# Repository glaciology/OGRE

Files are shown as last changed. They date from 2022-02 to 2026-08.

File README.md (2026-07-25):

<p align="center">

 
 </p>

# Open GNSS Research Equipment :: A low-power, low-cost GNSS data logger for monitoring the cryosphere.
<p align="center">

</p>

## Overview
Originally designed for easily logging multi-GNSS data in remote regions of the Arctic, this instruments incorporates low-power, low-cost components onto a single circuit board and features a Ublox ZED-F9P/X20P GNSS module and Ambiq Apollo3 MCU. By stripping away many of the features of commercial options, we streamline this instrument specifically for "set it and forget it" rapid deployments, acquiring high quality GNSS data.
- Logs GPS, GLONASS, BEIDOU, GALILEO & Satellite Nav Messages to a microSD, which can be easily converted to standard RINEX format (from .ubx) for positioning with PPK or PPP (RTK is possible but DIY). F9P variants (hardware v1.0) log L1/L2, X20P variant logs L1/L2/L5 (hardware v2.0). 
- Easily configurable via microSD card. Many configuration options to optimize data and battery needs, such as a polar-specific mode of daily logging during summertime and weekly logging during the winter, or a sunrise/sunset mode for logging data for 3 hours, twice daily to capture diurnal glacial signals. 
- Low cost, totaling ~$175, not including external components. PCB inside enclosure measures 7x6.5x2.5cm. 
- Current consumption with a 12V supply is 45-65mA (.5-.8W) awake, and 0.07mA (.8mW) asleep. We have used a single 12V 40Amp hr battery with a 10W solar panel to log continuously for 3 hours a day every day, including throughout the long polar night in Greenland.
- Programmed in Arduino environment, for easy customization.

A detailed guide is maintained [here](https://docs.google.com/document/d/1q8-jAFY2cO8MIOHwoCQhJwPjmURbkkGEsrDBrOs5gMM/edit?usp=sharing). 

<p align="center">

</p>

## Project Organization 
[Software: Contains Arduino Code and Test Scripts](Software/)
- [OGRE: Software and software config files for upload to OGRE instrument](Software/OGRE) <br>
[Hardware: Hardware & Manufacturing Files](Hardware/)
- Here you will find the component lists for OGREv1 and OGREv2. We recommend all future acquisitions use OGREv2, which is optimized for the X20P reciever. However, use v1 if you or your manufacturer cannot flash the device using a SWD/JTAG interface. See the firmware section for details on flashing the correct firmware onto your v1 or v2 device.  

Again, a detailed, up-to-date guide can found [here](https://docs.google.com/document/d/1q8-jAFY2cO8MIOHwoCQhJwPjmURbkkGEsrDBrOs5gMM/edit?usp=sharing)!

## Getting Started 

The OGRE has the following modes of operation (note, not all modes are available on old versions of the firmware, upgrade may be necessary): 
  - (1) Daily Fixed Mode: Log GNSS data same time every day, starting & ending during USER-defined start/stop hours, OR
  - (2) Continous Mode: Log GNSS data continously (new file generated at each midnight UTC), OR
  - (3) Monthly Mode: Log GNSS data for 24 hours on a USER-specified day (1-28) each month, OR
  - (4) Interval Mode: Each 24-hour log session is spaced by a USER-defined interval (e.g., log every 3 days for 24 hours), OR
  - (5) Log GNSS data for 24 hours on USER specified dates/times read from a .txt file. Defaults to mode 4 after last user-provided date.
  - (6) Log GNSS data for 24 hours; During winter once on every Nth day (or USER-defined interval, in # of days); During summer daily. "Summer" is May-August (or USER-defined months).
  - (7) Reserved.
  - (8) Log GNSS data twice daily for USER specified duration, during-USER defined morning period and USER-defined evening. 
  - (99) Test Mode: Used for development. Log GNSS data for 50 second interval, sleep for 50 second and repeat.
  
OUTPUTs: With all modes, GNSS data (phase, doppler, SNR, nav message etc.) are logged to a uSD card in .ubx (UBLOX) proprietary format. Under open sky conditions, we found that an epoch of data (1s) is ~2000-3000 bytes. If logging at 15 seconds for a year, this equates to 6GB of data. A debug file is also generated after each log session is closed, reporting the health of the system (temperature, battery voltage, logging errors, etc.). 
  
INPUTs: USERS specify settings in the CONFIG.txt file, which, if uploaded to the SD card, will be read into the software. If no CONFIG.txt exists on the attached SD card, it will automatically be added to the SD card with the default settings upon initial power-on.
Otherwise, software will default to hardcoded configuration. USER may also upload a EPOCH.txt file, which allows the user to specify up to 20 log dates (unix epoch format) for logging in Mode 5. The CONFIG.txt and EPOCH.txt files are Windows and Mac (e.g., Notepad or Textedit) compatable (previously, carriage return characters \n caused issues for Windows-generated files). Using an older CONFIG.txt version will not crash the OGRE, but will cause the OGRE to use the default settings instead. 

The CONFIG.TXT file is formatted as follows (make sure to use the right version, or let the device auto-populate the template onto your SD card): 

```
LOG_MODE(1: daily hr, 2: cont, 3: mon, 4: 24 roll, 5: date, 6: season, 99: test)=2
LOG_START_HOUR_UTC(mode 1 only)=17
LOG_END_HOUR_UTC(mode 1 only)=23
LOG_START_DAY(mode 3 only, 0-28)=25
LOG_EPOCH_SLEEP(modes 4/5 only, seconds)=3600
LED_INDICATORS(0-false, 1-true)=1
MEASURE_BATTERY(0-false, 1-true)=0
ENABLE_GPS(0-false, 1-true)=1
ENABLE_GLO(0-false, 1-true)=1
ENABLE_GAL(0-false, 1-true)=1
...
...
...
...
```

- If the USER selects LOG_MODE=1, then LOG_START_HOUR_UTC and LOG_END_HOUR_UTC must be specified. 
- If the USER selects LOG_MODE=3, then LOG_START_DAY must also be specified (day of each month GNSS data is logged). 
- If the USER selects LOG_MODE=5, then unix epoch dates for logging are specified in EPOCH.txt. If no dates are specified or if all dates have elapsed, then log interval defaults to LOG_MODE 4, where LOG_EPOCH_SLEEP must be defined.
- If the USER selects LOG_MODE=6, the instrument logs continuously during SUMMER_START_MONTH + SUMMER_START_DAY through SUMMER_END_MONTH + SUMMER_END_DAY (inclusive). Furthermore, the duration between logging during winter is set by WINTER_INTERVAL. Note: log sessions are 24 hours.
- If the USER selects LOG_MODE=8, then LOG_START_HOUR_UTC and LOG_END_HOUR_UTC must be specified, along with LOG_START_HR_TWO and LOG_END_HR_TWO. 
- LED_INDICATORS, if false, will disable all LEDs, excluding those present during initialization. 
- MEASURE_BATTERY, if true, battery voltage is measured/monitored, and the instrument will be put to sleep when voltage dips below 10.9V (OR as defined by user in BAT_SHUTDOWN_V). System will restart when voltage measured above ~11.2V (or 0.5V above BAT_SHUTDOWN_V). 
- STATION_NAME is a number between 0000 and zzzz (no special characters, please!), and will be appended to the timestamped file names for each GNSS file.
- MEASURE_RATE is frequency of epoch solutions logged to SD card: 1 = 1 solution per second, 15 = 1 solution per 15 seconds. Range is .5 to 60 (seconds). 

BASIC OPERATION:  
Insert the uSD card (with or without CONFIG & EPOCH files), then connect battery to +/- sides of the screw terminal. The system will attempt to initialize and following LED indicators will flash: 
  - 1 Hz Blinks: System acquiring GPS time and attempting to sync real time clock (RTC).
  - 10 rapid Blinks: System Configuration Complete!
  
 The following LED patterns indicate success or failure for OGREv2. For OGREv1, there is only 1 led. 
| Pattern | Meaning | Color (v2) | Triggered From |
|---|---|---|---|
| 2 blink pattern, then waits for reset | microSD card failed to initialize (twice) | 🔴 Red (`LED`) | `configureSD()` |
| 3 blink pattern, then waits for reset | u-blox I2C not detected, or GNSS constellation config failed | 🔴 Red (`LED`) | `configureGNSS()` |
| 5 blink pattern, then waits for reset | RTC failed to sync with GNSS within 3-minute window | 🔴 Red (`LED`) | `syncRtc()` |
| 6 rapid blinks | `CONFIG.TXT` missing/unreadable — using hard-coded defaults | 🔴 Red (`LED`) | `getConfig()` |
| 10 blinks | RTC synced + system configuration complete (boot only) | 🟡 Yellow (`LED2`) | `setup()` |
| 1 blink, roughly every 12 seconds | Device sleeping between sessions | 🔴 Red (`LED`) | `loop()` |
| 1 Hz blink | Acquiring GNSS fix during RTC sync | 🟡 Yellow (`LED2`) | `syncRtc()` |
| Rapid, irregular blinks while active, approx. corresponding to logging rate | Actively logging GNSS data to SD | 🔴 Red (`LED`) | `logGNSS()` |
| No blinks at all | Deep sleep — battery below shutdown threshold | *(none — both LEDs off)* | `checkBattery()` / `goToSleep()` |

## Software Upload
For OGREv1, software is uploaded using a USB-to-Serial converter. 
For OGREv2, software is uploaded using JTAG/SWD, or, if the proper bootloader is installed on the MCU, can be done over USB-to-Serial.

Only do this if you want to update the firmware on the OGRE, or if the OGRE has not yet had the firmware installed. A pre-compiled binary file is available with each release (see [releases](https://github.com/glaciology/OGRE/releases/)). Note: there are separate binaries for v1 and v2 OGREs. This binary file included in the release can be uploaded to the Apollo MCU (OGREv1) with a usb-to-serial cable connected to the PCB header pins using the Sparkfun Apollo3 Uploader [here](https://github.com/sparkfun/Apollo3_Uploader_SVL). 

For v2 OGREs, please reach out to me if you have questions that come up. The HARDWARE_VERSION macro must be set properly when manually compiling the code.

### OGRE V1
The USB to Serial converter is attached to the OGRE via the 5 through-hole pins on the PCB: attach Ground to GND, RX -> TX, TX->RX, etc. NOTE: the serial converter must be 3.3V. DO NOT EXPOSE pins to 5V. 

Example command line prompt using the svl.py script: [use baud -b 115200; provide path to binary file OGRE.ino.bin; find path of usb serial converter port by typing ls /dev/tty.* on Linux and selecting the proper usb port.] 
```
python3 svl.py -b 115200 -f /PATH/TO/BINARY/FILE/OGRE.ino.bin /dev/tty.usbserial-####
```

You can also compile the source code with the Arduino IDE, ensuring that the code and board libraries match the proper versions defined in the header of OGRE.ino [Sparkfun Artemis Module v1.2.3, SDFat library v2.1.0, Sparkfun ublox GNSS library v2.2.8]. 

### OGRE V2
If the bootloader is installed on OGRE v2, you can follow the above steps (same as OGRE v1). Otherwise, or if you don't know what I mean by this, you'll have to use JTAG/SWD. More details to come...

## Hardware Notes
<p align="center">

</p>

MATERIALS
Cost of PCB and all components totals ~$175. Detailed list of components found in the Hardware folder. <br>

ASSEMBLY
Assembly services are available through PCBWay, and the OGRE can be ordered directly from [here](https://www.pcbway.com/project/shareproject/OGRE_Open_GNSS_Research_Equipment_Receiver_33a809f3.html) for V1 or from [here](https://www.pcbway.com/project/shareproject/OGRE_Open_GNSS_Research_Equipment_v2_0_82247d12.html) for V2. Note that this assembly service often does not include the [Pololu](https://www.pololu.com/product/3792) component, which must be soldered (4 through-hole) by the user (requests may be made to PCBWay to see if they can source this component, or the user can ship to PCBWay). The user must also program the device following the instructions from the Software Upload section. OGRE2.0 (with ublox X20P) can similarly be ordered from [here](https://www.pcbway.com/project/shareproject/OGRE_Open_GNSS_Research_Equipment_v2_0_82247d12.html), and we highly recommend the customer asks PCBWay to upload the .bin firmware to the board using their JTAG/SWD interface. Instructions for PCBWay upload can be found [in Upload_Instructions](/Hardware/OGRE_v2.0/). 

If you choose to use a u-blox antenna, you will need a ground plane, which you can make out of any metal disc, or you can order pre-drilled discs from PCBWay too, [here](https://www.pcbway.com/project/shareproject/Ground_Plane_for_ublox_L1_L2_L5_GNSS_antenna_c3519487.html), compatitble for both L1/L2 and L1/L2/L5 versions of their antennas.

POWER REQUIREMENTS: 
In standard configuration, this system is powered by a 12V lead-acid battery. 
  
While this system is optimized for 12V batteries, input voltage can range from 5.2V to 20V with the following considerations/customizations:  
  - The DC-DC converter minimum input is 5.2V and maximum input is 50V, although additional power filtering at high voltages is required. 
  - The Battery Measurement circuit features a voltage divider circuit that must scale max voltage to 3.3V for the ADC pin. Standard dividers for a 12V battery use 68kOhm and 10kOhm resistors. USER may wish to adjust gain/offset of ADC battery measurement conversion in software if using non-standard (5.2-20V) power configuration. 
  - The reverse polarity protection MOSFET has a limit of 20V. **Do not exceed 20V** without either removing this part or finding an appropriate substitute component. 

## License & Credits
This project is open source! OGRE software is released under the [MIT License](http://opensource.org/licenses/MIT).

Portions of this code for this project are derived from [Sparkfun GNSS Library](https://github.com/sparkfun/SparkFun_u-blox_GNSS_Arduino_Library) [Sparkfun Arduino Core](https://github.com/sparkfun/Arduino_Apollo3/releases/tag/v1.2.0), [Sparkfun OpenLog GNSS](https://github.com/sparkfun/OpenLog_Artemis_GNSS_Logger), and
[Cryologger Glacier Velocity Tracker v2.0.3](https://github.com/adamgarbo/Cryologger_Glacier_Velocity_Tracker).

Modifications Copyright (c) 2020 SparkFun
Modifications Copyright (c) 2020 Adam Garbo

See [License](LICENSE.md) for more details.

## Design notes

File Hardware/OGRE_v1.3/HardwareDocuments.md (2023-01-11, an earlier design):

**Documentation of Critical Parts Found on OGRE:** 

[MCU: Apollo 3-Integrated on Sparkfun Artemis-Datasheet](https://ambiq.com/wp-content/uploads/2020/10/Apollo3-Blue-SoC-Datasheet.pdf)

[MCU: Sparkfun Artemis Integration Guide](https://cdn.sparkfun.com/assets/8/7/5/3/f/Artemis_Integration_Guide.pdf)

[GNSS: ZED-F9P Integration Manual](https://content.u-blox.com/sites/default/files/ZED-F9P_IntegrationManual_UBX-18010802.pdf)

[Power: Pololu 5V 600mA Buck Converter](https://www.pololu.com/product/3792)

[Battery: Deka 8G40 40Ahr Lead Acid Battery Datasheet](https://www.sunwize.com/wp-content/uploads/2020/03/8G40-DEKA.pdf)

[Battery: 8G40 Safety Data Sheet](https://www.eastpennmanufacturing.com/wp-content/uploads/Non-Spillable-Batteries.pdf)

[Solar: Ameresco 10M 10W Solar Panel Data Sheet](https://www.amerescosolar.com/wp-content/uploads/Ameresco-Solar-10M-10W_0.pdf)

[Solar: GV-5 Charge Controller Data Sheet](https://sunforgellc.com/wp-content/uploads/2022/04/GV-5_Datasheet-2018.pdf)

[Solar: GV-5 Charge Controller Manual](https://sunforgellc.com/wp-content/uploads/2022/04/GV-5_Manual.pdf)

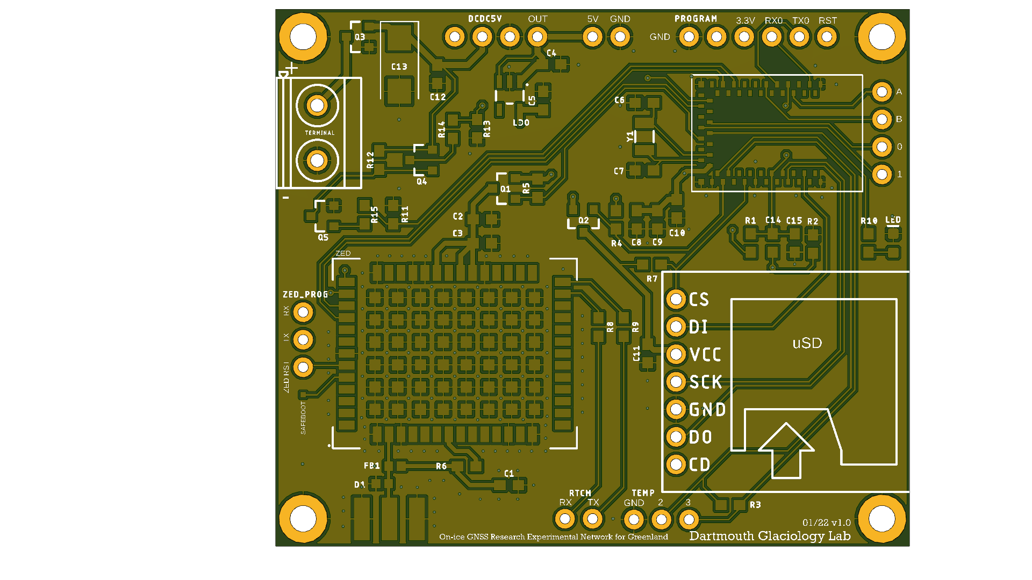
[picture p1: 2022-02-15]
Hardware/Silkscreen.png

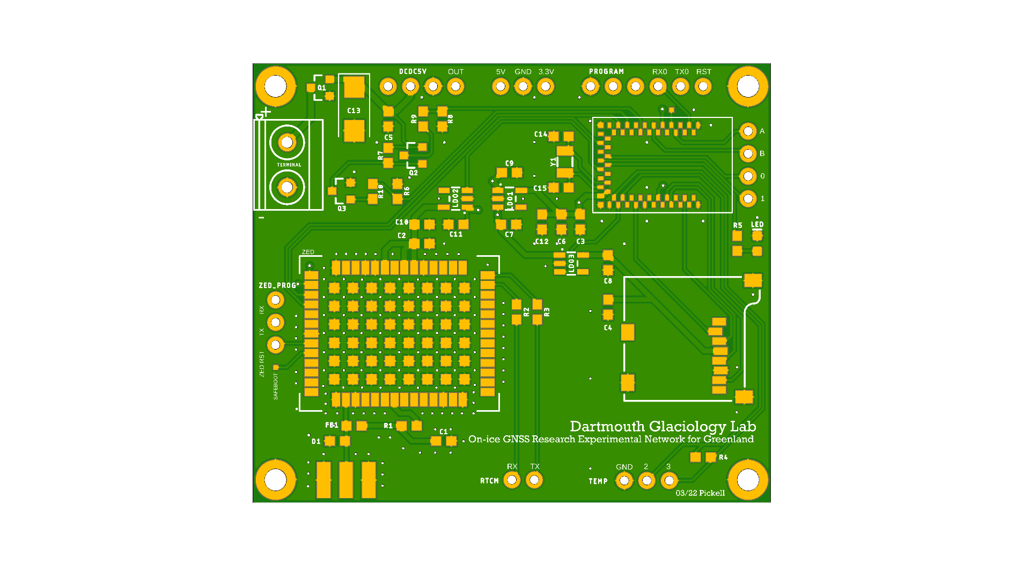
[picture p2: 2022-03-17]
Hardware/GNSS_PCB2_Silkscreen.png

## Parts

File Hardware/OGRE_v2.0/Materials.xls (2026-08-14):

Item # | Designator | Qty/Brd | Manufacturer | Mfg Part # | Description/Value | Package/Footprint | Mounting Type | Category | Instructions / Notes | Substitute | *Unit Price (est) | Notes/Substitutes
1 | ZED | 1 | u-blox | ZED-X20P-00B | ZED-X20P-00B | ZED-F9P | SMD | Ublox |  | Y-with caution | $186.980 | ZED-F9P-0XX is L1/L2 only, but much cheaper (150$). OR ZED-F20P is L1/L2/L5
2 | MCU | 1 | Ambiq | AMA3B1KK-KQR-B0 | RF System on a Chip - SoC Cortex-M4F 96MHz, 1MB Flash, 384KB SRAM, BLE5, 64-pin QFN, B0 | QFN40P800X800X80-65N | SMD | MCU |  | N | $8.925
3 | C1 | 1 | KEMET | C0603C470J5RAC7867 | CAP CER 47PF 50V X7R 0603 | 0603 | SMD | Antenna Circuit |  | Y | $0.263
4 | FB1 | 1 | Murata Electronics | BLM18AG121SH1D | FERRITE BEAD 120 OHM 0603 1LN | 0603 | SMD | Antenna Circuit |  | Y | $0.336
5 | D1 | 1 | Littelfuse Inc. | PESD0603-240 | TVS DIODE 24VWM 45VC 0603 | 0603 | SMD | Antenna Circuit |  | Y | $0.180
6 | R1 | 1 | Bourns Inc. | CR0603-FX-33R0ELF | RES SMD 33 OHM 1% 1/10W 0603 | 0603 | SMD | Ublox Resistors |  | Y | $0.053
7 | LDO1, LDO2, LDO3 | 3 | Richtek USA Inc. | RT9080-33GJ5 | IC REG LIN 3.3V 600MA TSOT23-5 | SOT23-5 | SMD | Power |  | Y | $0.203
8 | C13 | 1 | KEMET | T491C226K025AT | CAP TANT 22UF 10% 25V 2312 | CAP TANT 22UF 10% 25V 2312 | SMD | Capacitors | Polarized - see instructions | Y | $0.394
9 | C12 | 1 | Samsung Electro-Mechanics | CL10X106MQ8NNNC | CAP CER 10UF 6.3V X6S 0603 | 0603 | SMD | Capacitors |  | Y | $0.053
10 | C10, C11, C7, C8, C9 | 5 | Samsung Electro-Mechanics | CL10A105KO8NNNC | CAP CER 1UF 16V X5R 0603 | 0603 | SMD | Capacitors |  | Y | $0.010
11 | C2, C3, C4, C5 | 4 | KEMET | C0603C104J3RACAUTO | CAP CER 0.1UF 25V X7R 0603 | 0603 | SMD | Capacitors |  | Y | $0.105
12 | C27, C28 | 2 | KEMET | C0603C150J5GAC7867 | CAP CER 15PF 50V C0G/NP0 0603 | 0603 | SMD | RTC |  | Y | $0.158
13 | Y1 | 1 | TXC CORPORATION | 9HT10-32.768KDZF-T | CRYSTAL-32.768KHZ, SMD-3.2X1.5 | CRYSTAL-SMD-3.2X1.5MM | SMD | RTC |  | Y | $1.425
14 | LED | 1 | Vishay Semiconductor Opto Division | TLMS1000-GS15 | LED RED 0603 SMD | LED-0603 | SMD | LED | Polarized - see instructions | N | $0.362
15 | LED2 | 1 | Vishay Semiconductor Opto Division | TLMY1000-GS15 | LED YELLOW 0603 SMD | LED-0603 | SMD | LED | Polarized - see instructions | N | $0.555
16 | Q1, Q2 | 2 | Infineon Technologies | IRLML5203TRPBF | MOSFET P-CH 30V 3A MICRO3/SOT23 | SOT23-4 | SMD | MOSFET |  | N | $0.262
17 | Q3 | 1 | Infineon Technologies | SMBT2222AE6327HTSA1 | TRANS NPN 40V 0.6A SOT23 | SOT23-3 | SMD | TRANSISTOR |  | N | $0.637
18 | Screw Terminal | 1 | Phoenix Contact | 277-1247-ND | TERM BLK 2P SIDE ENT 5.08MM PCB | 0.200 (5.08mm) | TH | Power | 2 pin TH, see instructions | Y | $1.061
19 | E1-SMA | 1 | Sparkfun | WRL-00593 | SparkFun Accessories SMA Connector | Edge | Edge | Antenna Circuit | see instructions, see notes | Y-with caution | $4.299 | Taoglass EMPCB.CSMAFSTJ.A $4.00
20 | J1 | 1 | Sparkfun | PRT-00127 | MICRO-SD-SOCKET | MICRO-SD-SOCKET | SMD | uSD |  | Y-with caution | $1.210 | GCT 640-MEM20610118800A (pads slightly misaligned, check reflow first) $1.00
21 | R2, R3 | 0 | DNP | DNP | DNP | 0603 | SMD | ZED
22 | R6, R7, R8 | 3 | Bourns Inc. | CR0603-FX-1002ELF | RES SMD 10K OHM 1% 1/10W 0603 | 0603 | SMD | Resistors |  | Y | $0.025
23 | R10 | 1 | Bourns Inc. | CR0603-FX-1001ELF | RES SMD 1K OHM 1% 1/10W 0603 | 0603 | SMD | Resistors |  | Y | $0.053
24 | R11 | 1 | Bourns Inc. | CR0603-FX-1003ELF | RES SMD 100K OHM 1% 1/10W 0603 | 0603 | SMD | Reset |  | Y | $0.053
25 | R4, R5 | 2 | Bourns Inc. | CR0603-FX-4701ELF | RES SMD 4.7K OHM 1% 1/10W 0603 | 0603 | SMD | LED |  | Y | $0.032
26 | R9 | 1 | Bourns Inc. | CR0603-FX-6802ELF | RES SMD 68K OHM 1% 1/10W 0603 | 0603 | SMD | Battery |  | Y | $0.053
27 | C26 | 1 | KEMET | C0603X102K5RAC3316 | CAP CER 0603 1NF 50V X7R 10% | 0603 | SMD | Reset |  | Y | $0.368
28 | Pololu | 1 | Pololu | 2183-3792-ND/5V, 600mA Step-Down Voltage Regulator D36V6F5 | DC DC CONVERTER 5V 3W | 4 pin through hole | TH | Power | 4 pin TH, see instructions | N | $6.000
29 | C20, C21, C22, C23 | 4 | Murata Electronics | GRT155R61A225KE01J | 2.2uF | 0402-TIGHT | SMD | Capacitors |  | Y | $0.111
30 | C14, C15, C16, C17, C18, C19, C6 | 7 | Murata Electronics | GXT155R61C105KE01D | 1.0uF | 0402-TIGHT | SMD | Capacitors |  | Y | $0.199
31 | C25 | 1 | Murata Electronics | GXT155R60J474KE01D | 0.47uF | 0402-TIGHT | SMD | Capacitors |  | Y | $0.337
32 | L1 | 1 | Murata Electronics | DFE201612E-2R2M=P2 | 2.2uH | 0805-WIDE | SMD | Inductors |  | Y | $0.308
33 | C24 | 1 | TAIYO YUDEN | MCASJ105BB5475MFNA1J | 4.7uF | 0402-TIGHT | SMD | Capacitors |  | Y | $0.483

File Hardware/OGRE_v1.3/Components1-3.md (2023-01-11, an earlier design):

| Class           | Component            | Quantity/BRD | Description                                 | Part #              |
|-----------------|----------------------|--------------|---------------------------------------------|---------------------|
| Ublox           | ZED-F9P-02B          | 1            | ZED-F9P-02B (-04B, F9T- versions also OK)   | ZED-F9P-02B         |
| MCU             | Apollo-3 Artemis     | 1            | Sparkfun Artemis Module                     | WRL-15484           |
| Antenna Circuit | C1                   | 1            | 47PF-0603-50V-5%                            | C0603C470J5RAC7867  |
| Antenna Circuit | E1-SMA               | 1            | SMA male connector                          | WRL-00593           |
| Antenna Circuit | FB1                  | 1            | Ferrite Bead-120OHM-0603                    | BLM18AG121SH1D      |
| Antenna Circuit | D1                   | 1            | ESD protection diode                        | PESD0603-240        |
| Ublox Resistors | R1, R2, R3           | 3            | 33KOHM-0603-1/10W-1%                        | CR0603-FX-33R0ELF   |
| Power           | Screw Terminal       | 1            | 2 port screw terminal                       | 277-12547-ND        |
| Power           | Pololu Switch        | 1            | 5V Step Down Converter, 600mA               | D36V6F3             |
| Power           | LDO                  | 3            | IC REG LIN 3.3V 600MA TSOT23-5              | RT9080-33GJ5        |
| Capacitors      | C13                  | 1            | 22 UF Tantalum Capacitor-2412 (6032-METRIC) | T491C226K025AT      |
| Capacitors      | C12                  | 1            | 10UF-0603-6.3V-20%                          | CL10X106MQ8NNNC     |
| Capacitors      | C6, C7, C8, C9, C10, C11  | 6       | 1.0UF-0603-16V-10%                          | CL10A105KO8NNNC     |
| Capacitors      | C2, C3, C4, C5       | 4            | 0.1UF-0603-25V-5%                           | C0603C104J3RACAUTO  |
| RTC             | C14, C15             | 2            | 15PF-0603-50V-5%                            | C0603C150J5GAC7867  |
| RTC             | Y1                   | 1            | CRYSTAL-32.768KHZ, SMD-3.2X1.5              | 12.87156 (digikey)  |
| LED             | LED                  | 1            | 1.8 Vf, 2 mA                                | TLMS1000-GS08       |
| TRANSISTOR      | Q3                   | 1            | TRANS NPN 30V 600MA SOT23-3                 | SMBT2222AE6327HTSA1 |
| MOSFET          | Q4, Q5               | 2            | Battery Switch, Reverse Polarity Protection | TSM3401CX RFG       |
| Temp, LED?      | R4 (optional), R5    | 1 or 2       | 4.7KOHM-0603-1/10W-1%                       | CR0603-FX-4701ELF   |
| Battery         | R6, R7, R8           | 3            | 10KOHM-0603-1/10W-1%                        | CR0603-FX-1002ELF   |
| Battery         | R9                   | 1            | 68KOHM-0603-1/10W-1%                        | CR0603-FX-6802ELF   |
| Battery         | R10                  | 1            | 1KOHM-0603-1/10W-1%                         | CR0603-FX-1001ELF   |
| Antenna         | Antenna              | 1            | UBLOX SMA Powered                           | ANN-MB              |
| uSD             | uSD                  | 1            | microSD Socket                              | PRT-00127           |
| Reset Circuit   | R11                  | 1            | 100KOHM-0603-1/10W-1%                       | CR0603-FX-1003ELF   | 
| Reset Circuit   | C16                  | 1            | 1.0nF-0603-50V-X7R-10%                      |C0603X102K5RAC3316   |

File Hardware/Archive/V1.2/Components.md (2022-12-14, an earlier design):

| Class           | Component            | Quantity/BRD | Description                                 | Part #              |
|-----------------|----------------------|--------------|---------------------------------------------|---------------------|
| Ublox           | ZED-F9P-02B          | 1            | ZED-F9P-02B                                 | ZED-F9P-02B         |
| MCU             | Apollo/Artemis       | 1            | Sparkfun Artemis Module                     | WRL-15484           |
| Antenna Circuit | C1                   | 1            | 47PF-0603-50V-5%                            | ‎C0603C470J5RAC7867‎|
| Antenna Circuit | E1-SMA               | 1            | SMA male connector                          | WRL-00593           |
| Antenna Circuit | FB1                  | 1            | Ferrite Bead-120OHM-0603                    | BLM18AG121SH1D      |
| Antenna Circuit | D1                   | 1            | ESD protection diode                        | PESD0603-240        |
| Ublox Resistors | R1, R2, R3           | 3            | 33KOHM-0603-1/10W-1%                        | CR0603-FX-33R0ELF   |
| Power           | Screw Terminal       | 1            | 2 port screw terminal                       | 277-1247-ND         |
| Power           | Pololu Switch        | 1            | 5V Step Down Converter, 600mA               | D36V6F3             |
| Power           | LDO                  | 3            | IC REG LIN 3.3V 600MA TSOT23-5              | RT9080-33GJ5        |
| Capacitors      | C13                  | 1            | Tantalum Capacitor-2412 (6032-METRIC)       | C0603X102K5RAC3316  |
| Capacitors      | C12                  | 1            | 10UF-0603-6.3V-20%                          | CL10X106MQ8NNNC     |
| Capacitors      | C7, C8, C9, C10, C11 | 5            | 1.0UF-0603-16V-10%                          | ‎CL10A105KO8NNNC‎   |
| Capacitors      | C2, C3, C4, C5       | 4            | 0.1UF-0603-25V-5%                           | C0603C104J3RACAUTO  |
| RTC             | C14, C15             | 2            | 15PF-0603-50V-5%                            | C0603C150J5GAC7867  |
| RTC             | Y1                   | 1            | CRYSTAL-32.768KHZ, SMD-3.2X1.5              | ‎12.87156‎ (digikey)|
| LED             | LED                  | 1            | 1.8 Vf, 2 mA                                | TLMS1000-GS08       |
| TRANSISTOR      | Q3                   | 1            | TRANS NPN 30V 600MA SOT23-3                 | SMBT2222AE6327HTSA1 |
| MOSFET          | Q4, Q5               | 2            | Battery Switch, Reverse Polarity Protection | TSM3401CX RFG       |
| Temp, LED?      | R4, (R5?)            | 1            | 4.7KOHM-0603-1/10W-1%                       | CR0603-FX-4701ELF   |
| Battery         | R5, R6, R7, R8       | 4            | 10KOHM-0603-1/10W-1%                        | ‎CR0603-FX-1002ELF‎ |
| Battery         | R9                   | 1            | 68KOHM-0603-1/10W-1%                        | CR0603-FX-6802ELF   |
| Battery         | R10                  | 1            | 1KOHM-0603-1/10W-1%                         | CR0603-FX-1001ELF   |
| Antenna         | Antenna              | 1            | UBLOX                                       | ANN-MB              |
| uSD             | uSD                  | 1            | microSD Socket                              | PRT-00127           |
| Reset Circuit   | R11                  | 1            | 100KOHM-0603-1/10W-1%                       | CR0603-FX-1003ELF   | 
| Reset Circuit   | C16                  | 1            | 1.0nF-0603-50V-X7R-10%                      |C0603X102K5RAC3316   |

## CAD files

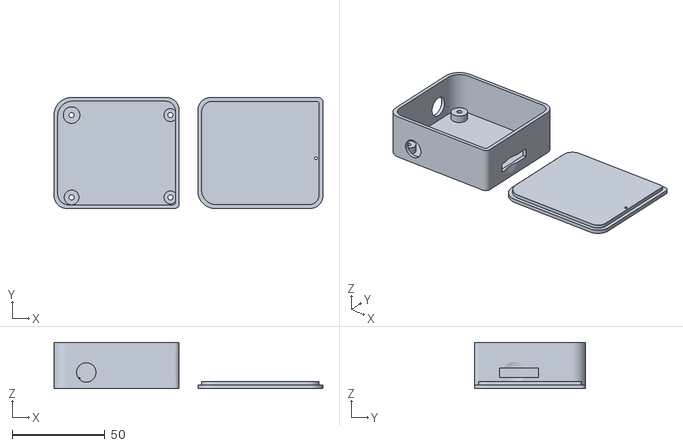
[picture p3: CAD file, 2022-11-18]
Hardware/PLA_Enclosure/Enclosure.stl
145.4 x 60.0 x 25.0

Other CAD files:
Hardware/Archive/V1.1/OGRENET_CAD.f3z
Hardware/OGRENET_CAD.f3z

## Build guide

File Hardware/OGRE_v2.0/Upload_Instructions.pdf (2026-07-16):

Programming Instructions: OGRE v2, when newly manufactured, can only be interfaced with a SWD/JTAG.

Within the SWD/JTAG environment, execute the following:

Setup: Apply power to PCB by connecting 5V source to 5V pin, and ground to GND pin (see attached photo).

Connect J-Link to the target device via SWD interface at 4000 kHz

Verify target voltage is present before attempting connection — if you see "Target voltage too low," check power to the device and retry.

In J-Link Commander on your computer, connect to device AMA3B1KK-KQR

Run the following command:**

loadbin <OGRE2.ino.bin> 0x0000C000

A successful flash will show:

J-Link: Flash download: Program & Verify speed: ~150 KB/s
O.K.

*note to user: replace OGRE2.ino.bin with any compiled Arduino script. For example, upload svl.bin from Sparkfun instead if you want to enable serial programmability to your device. Afterwards, you can upload any Arduino script using the serial interface instead of SWD (https://github.com/sparkfun/Apollo3_Uploader_SVL/tree/main/bootloader/gcc/artemis_module/bin)

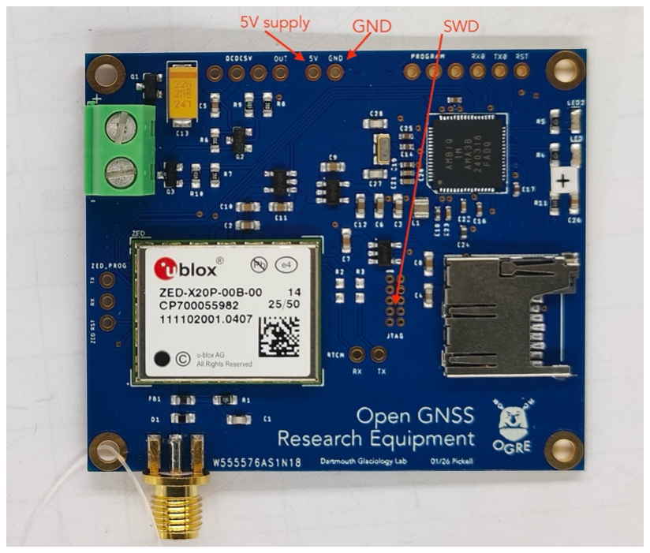
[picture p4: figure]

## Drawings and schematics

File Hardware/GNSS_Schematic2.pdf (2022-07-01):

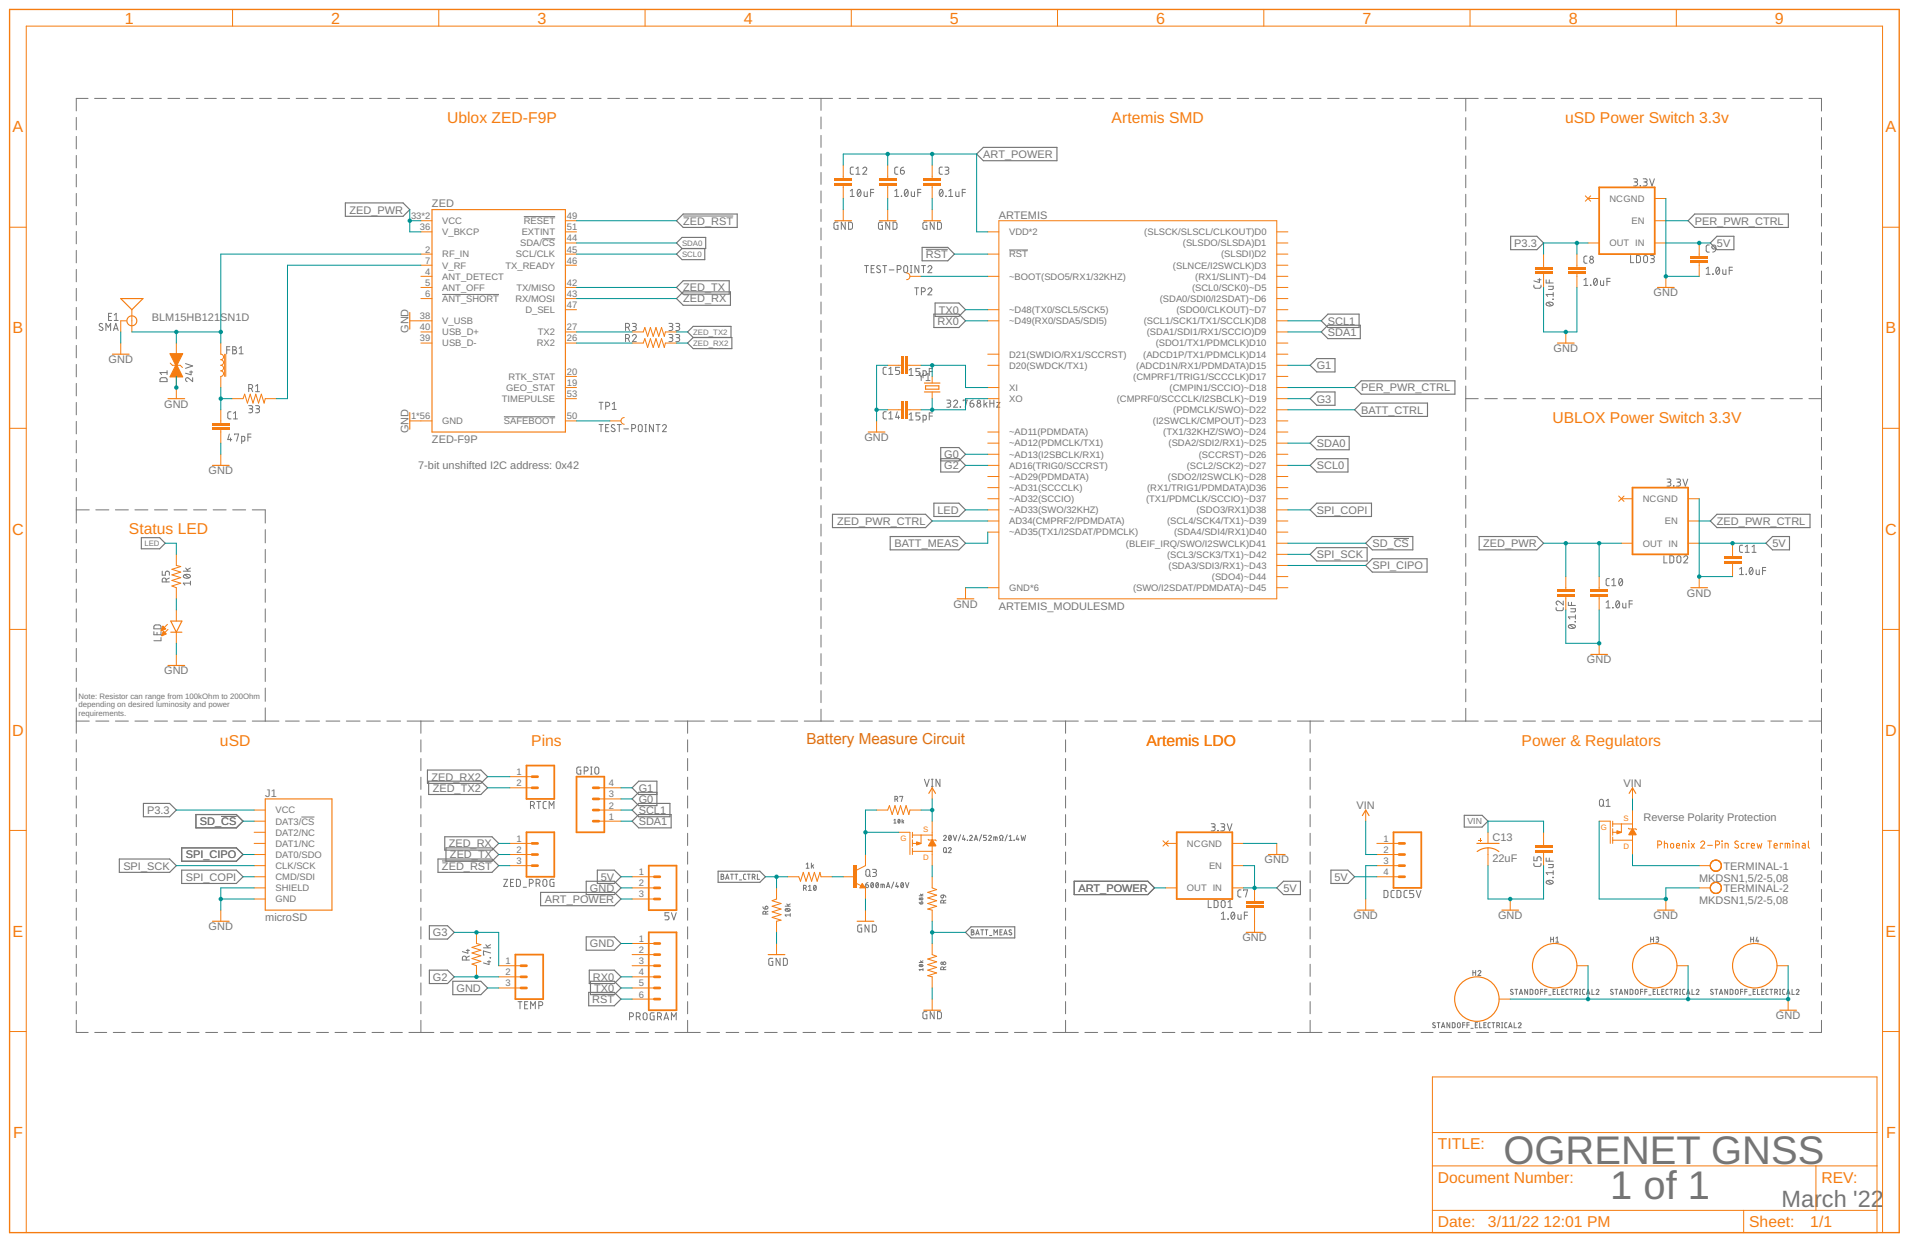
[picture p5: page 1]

AD16(TRIG0/SCCRST) ~AD29(PDMDATA) ~AD31(SCCCLK) ~AD32(SCCIO)

Note: Resistor can range from 100kOhm to 200Ohm
depending on desired luminosity and power
requirements.

1 of 1 Document Number: March '22 | REV:

Date: 3/11/22 12:01 PM | Sheet: 1/1

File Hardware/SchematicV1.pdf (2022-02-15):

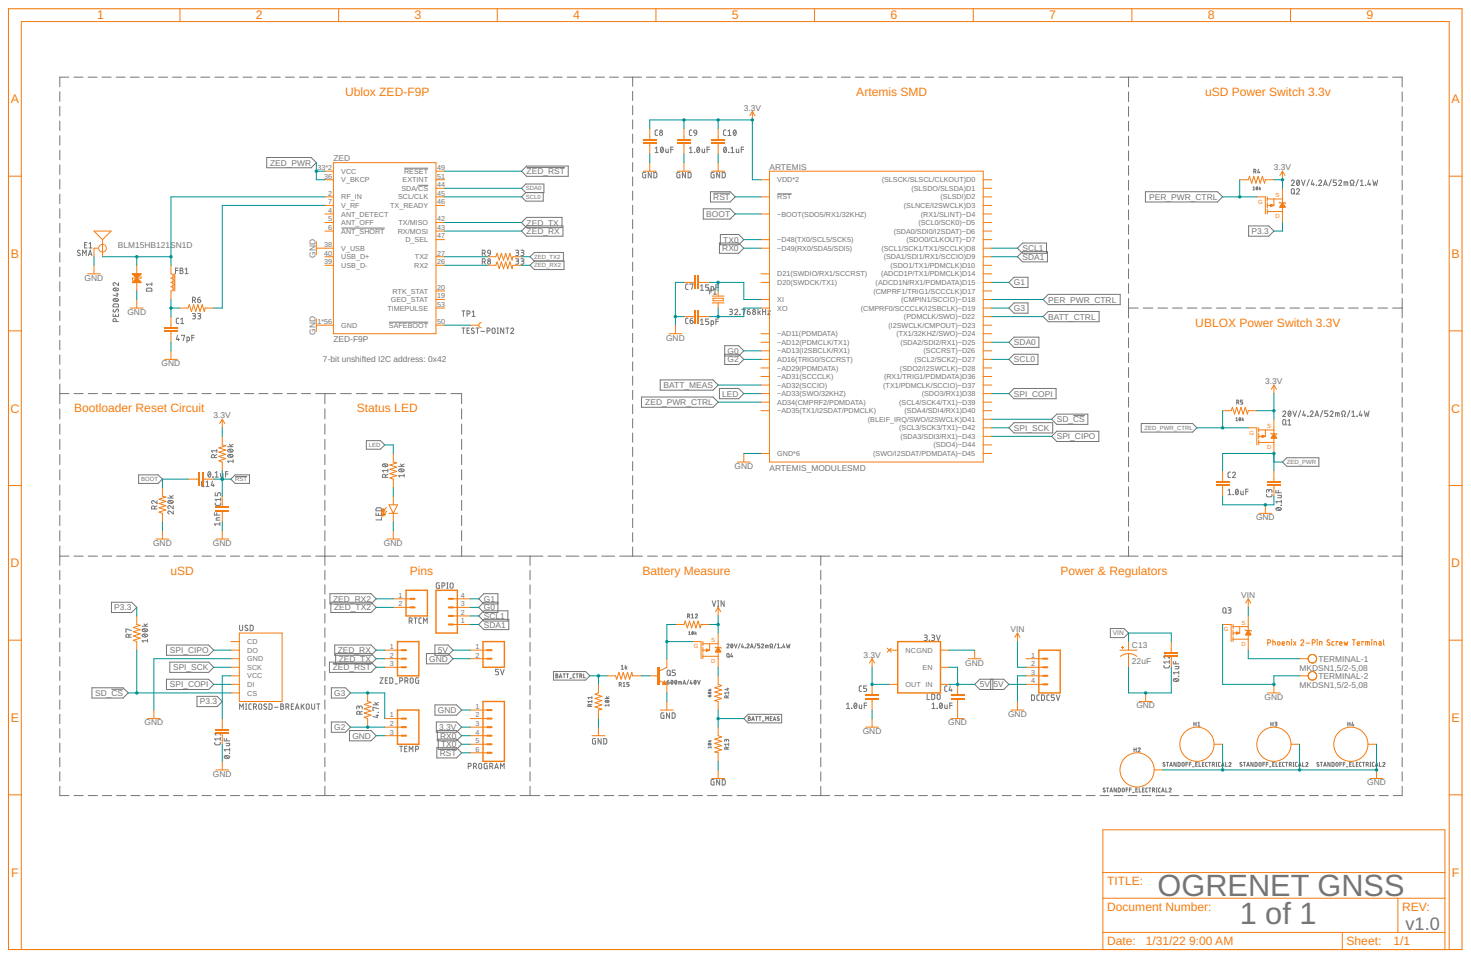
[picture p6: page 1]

~BOOT(SDO5/RX1/32KHZ) D21(SWDIO/RX1/SCCRST) D20(SWDCK/TX1)

~AD11(PDMDATA) ~AD12(PDMCLK/TX1) ~AD13(I2SBCLK/RX1) AD16(TRIG0/SCCRST) ~AD29(PDMDATA) ~AD31(SCCCLK) ~AD32(SCCIO) AD34(CMPRF2/PDMDATA) ~AD35(TX1/I2SDAT/PDMCLK)

IN GND OUT EN

1 of 1 Document Number: | REV: v1.0

Date: 1/31/22 9:00 AM | Sheet: 1/1

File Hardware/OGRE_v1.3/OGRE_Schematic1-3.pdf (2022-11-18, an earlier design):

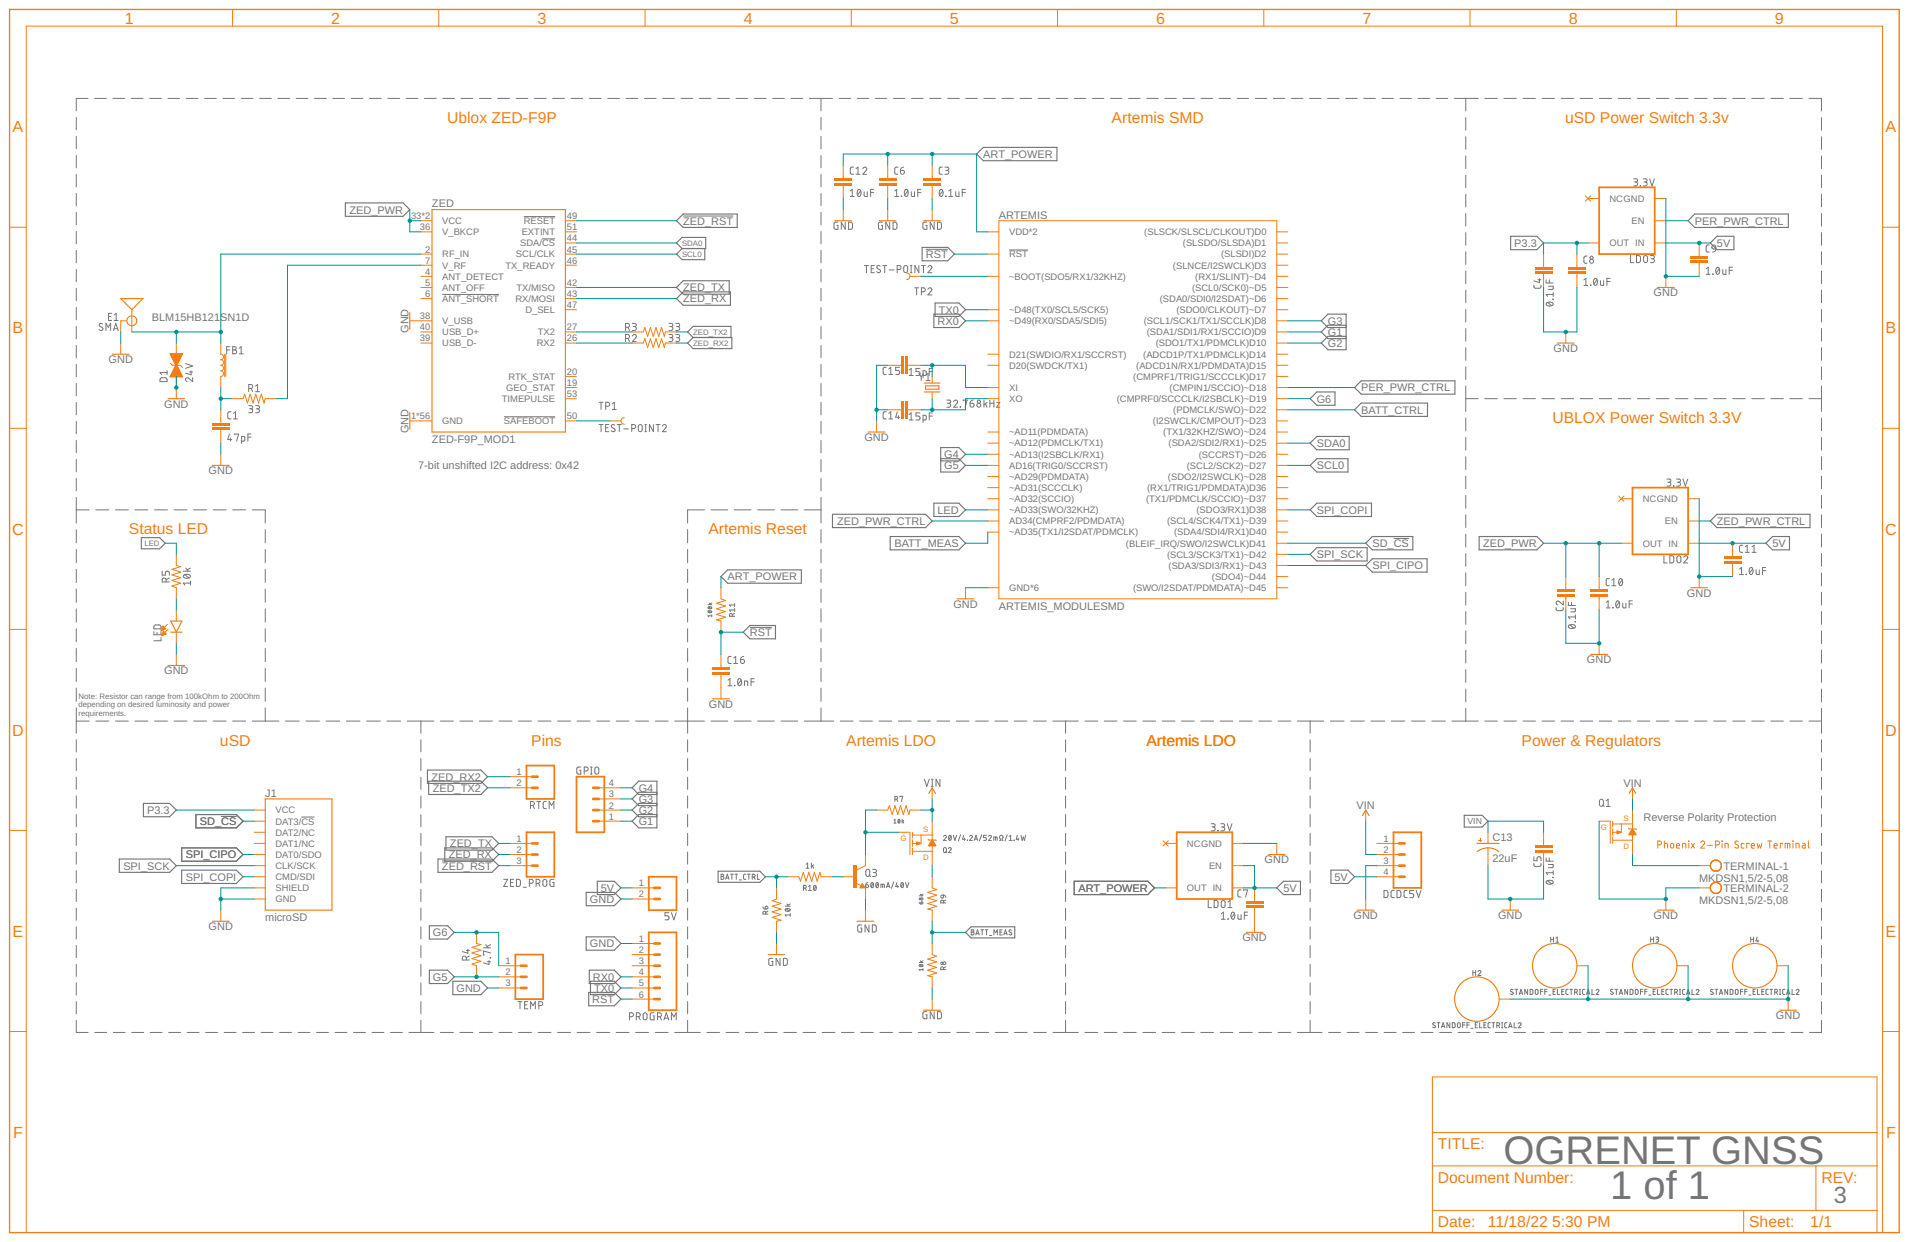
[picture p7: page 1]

AD16(TRIG0/SCCRST) ~AD29(PDMDATA) ~AD31(SCCCLK) ~AD32(SCCIO)

Note: Resistor can range from 100kOhm to 200Ohm
depending on desired luminosity and power
requirements.

1 of 1 Document Number: | REV: 3

Date: 11/18/22 5:30 PM | Sheet: 1/1

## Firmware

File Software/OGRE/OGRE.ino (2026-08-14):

/*
   OGRE: Open GNSS Research Equipment (On-ice GNSS Research Experimental Network for Greenland)
   Derek Pickell 06 Feb 2026
   V3.2.0

   Hardware:
   - OGRE PCB w/ ZED-F9P/T (Note: using -F9T, adjust L5 settings).
   - OGREv2 PCB w/ZED-X20P

   Dependencies:
   - SparkFun_u-blox_GNSS_Arduino_Library v2.2.8
   - Apollo3 Arduino Core v1.2.3
   - SdFat Library v2.1.0

   INSTRUCTIONS:
   - See github.com/glaciology/OGRENet/ for detailed instructions.
   - Optional settings files on SD card: CONFIG.txt, EPOCHS.txt
   - LED indicators:
         2 Blink Pattern: uSD failed - waiting for RESET
         3 Blink Pattern: Ublox I2C or config failed - waiting for RESET
         5 Blink Pattern: RTC sync fail - waiting for RESET
         6 Rapid Blinks: CONFIG file failed to read; using defaults
         10 Blinks: RTC synced and System Configuration COMPLETE (After Initial Power On or Reset Only)
         1 Blink every 12 seconds: Sleeping
         Random Rapid Blinks: System logging data.
         No Blinks: System deep sleep due to low battery or battery dead.

   Attributions:
   - Some code, structure and ideas adapted/modified from Sparkfun
   - and A. Garbo GVMS [Copyright (c) 2020 SparkFun, Copyright (c) 2020 Adam Garbo]
   - are dilineated in these pages, and further detailed in the documentation.
   - Libraries are detailed and attributed below.
   - This project is open source; see Readme/Licensing.
*/

#define HARDWARE_VERSION 1  // 1 = OGREv1 3/22 || 2 = OGREv2 2/26
#define SOFTWARE_VERSION "V3.2.0"
#define EPOCH_FILE 20
#define STAT_REGISTER_ADDRESS 0x4FFFF000
#define UNIQUE_ID_ADDRESS     0x40020004
volatile uint32_t *unique_chip_id = (uint32_t *)UNIQUE_ID_ADDRESS;

///////// LIBRARIES & OBJECT INSTANTIATIONS //////////
#include <Wire.h>                             // Apollo3 Arduino Core v1.2.3
#include <SPI.h>                              // ""
#include <WDT.h>                              // ""
#include <RTC.h>                              // ""
#include <SdFat.h>                            // https://github.com/greiman/SdFat v2.1.0
//#include <SparkFun_u-blox_GNSS_Arduino_Library.h>
//SFE_UBLOX_GNSS gnss;                          
#if HARDWARE_VERSION == 1
  #include <SparkFun_u-blox_GNSS_Arduino_Library.h> // Library v2.2.8: http://librarymanager/All#SparkFun_u-blox_GNSS
  SFE_UBLOX_GNSS gnss;
#elif HARDWARE_VERSION == 2
  #include <SparkFun_u-blox_GNSS_v3.h>              // Library v3.1.13:
  SFE_UBLOX_GNSS gnss;
#endif
SdFs sd;                                      // SdFs = supports FAT16, FAT32 and exFAT (4GB+), corresponding to FsFile class
APM3_RTC rtc;                                 //
APM3_WDT wdt;                                 //
FsFile myFile;                                // RAW UBX LOG FILE
FsFile debugFile;                             // DEBUG LOG FILE
FsFile configFile;                            // USER INPUT CONFIG FILE
FsFile dateFile;                              // USER INPUT EPOCHS FILE

///////// HARDWARE-SPECIFIC PINOUTS & OBJECTS ////////
#if HARDWARE_VERSION == 1
const byte BAT                    = 35;       // Measure Battery Voltage
const byte SHIELD                 = 19;       // Use with Telemetry Shield (v1 only)
const byte PER_POWER              = 18;       // Drive to turn off uSD
const byte ZED_POWER              = 34;       // Drive to turn off ZED
const byte LED                    = 33;       // LED
const byte BAT_CNTRL              = 22;       // Drive high to turn on Bat measure
TwoWire myWire(2);                            // USE I2C bus 2, SDA/SCL 25/27
#elif HARDWARE_VERSION == 2
const byte BAT                    = 12;       // Measure Battery Voltage
const byte PER_POWER              = 2;        // Drive to turn off uSD
const byte ZED_POWER              = 28;       // Drive to turn off ZED
const byte LED                    = 40;       // LED1 (red)
const byte LED2                   = 39;       // LED2 (yellow)
const byte BAT_CNTRL              = 7;        // Drive high to turn on Bat measure
TwoWire myWire(0);                            // USE I2C bus 0, SDA/SCL 5/6
#endif
const byte PIN_SD_CS              = 41;       //
SPIClass mySpi(3);                            // Use SPI 3 - pins 38, 42, 43
#define SD_CONFIG SdSpiConfig(PIN_SD_CS, DEDICATED_SPI, SD_SCK_MHZ(24), &mySpi)

//////////////////////////////////////////////////////
//--------- USER DEFAULT CONFIGURATION HERE ------------
// LOG MODE:
byte logMode                = 6;              // {1, 2, 3, 4, 5, 6, 99}

// LOG MODE 1/8: DAILY, DURING DEFINED HOURS
byte logStartHr             = 12;             // UTC Hour
byte logEndHr               = 16;             // UTC Hour

// LOG MODE 8: TWICE DAILY, DURING DEFINED HOURS
byte logStartHrTWO          = 16;             // UTC Hour
byte logEndHrTWO            = 19;             // UTC Hour

// LOG MODE 3: ONCE/MONTH FOR 24 HOURS
byte logStartDay            = 8;              // Day of month between 1 and 28

// LOG MODE 4/5: SLEEP FOR SPECIFIED DURATION
uint32_t epochSleep         = 518400;        // Sleep duration (Seconds) (i.e., 2628000 ~ 1 month, 518400 ~ 6 days)

// LOG MODE 6: SUMMER/WINTER: LOG 24 HOURS, SLEEP FOR:
uint32_t winterInterval     = 777600;         // Sleep duration during winter, i.e., 9 days
byte startMonth             = 4;              // Start month, inclusive (April)
byte endMonth               = 9;              // End month, inclusive (August)
byte startDay               = 21;             // Start day (of month), inclusive, e.g., Apr 21
byte endDay                 = 21;             // End day (of month), inclusive, e.g., Sep 21

// LOG MODE 99: TEST: ALTERNATE SLEEP/LOG FOR X SECONDS
uint32_t secondsSleep       = 50;             // Sleep interval (Seconds)
uint32_t secondsLog         = 50;             // Logging interval (Seconds)

// UBLOX MESSAGE CONFIGURATION:
int logGPS                  = 1;              // FOR EACH CONSTELLATION 1 = ENABLE, 0 = DISABLE
int logGLO                  = 1;              //
int logGAL                  = 1;              //
int logBDS                  = 1;              //
int logQZSS                 = 0;              //
int logSBAS                 = 0;              // Not on SD CONFIG File
int logNav                  = 0;              //
int logL5                   = 0;              // WARNING: only set if using L5-capable ZED.

// ADDITIONAL CONFIGURATION
bool ledBlink               = true;           // If FALSE, all LED indicators during log/sleep disabled
bool measureBattery         = false;          // If TRUE, uses battery circuit to measure V during debug logs
bool terminalLogging        = false;          // If TRUE, log raw ubx to terminal
char stationName[5]         = "0000";         // Station name, 4 digits
int  measurementRate        = 5;              // Produce a measurement every X seconds

// BATTERY PARAMETERS
float gain                   = 17.2;          // Gain/offset for 68k/10k voltage divider battery voltage measure
float offset                 = 0.23;          // ADC range 0-2.0V
float shutdownThreshold      = 10.9;          // Shutdown if battery voltage dips below this (10.8V for DEKA 12V GEL)
// SYSTEM WILL SLEEP IF DIPS BELOW HERE, WAKES after shutdownThreshold + 0.5V reached
//----------------------------------------------------
//////////////////////////////////////////////////////

///////// GLOBAL VARIABLES ///////////////////////////
const int     sdWriteSize         = 512;      // Write data to SD in blocks of 512 bytes
const int     fileBufferSize      = 16384;    // Allocate 16KB RAM for UBX message storage
bool          summerInterval      = false;    // LM 6 only: when true, it's summer so it logs continuously
volatile bool wdtFlag             = false;    // ISR WatchDog
volatile bool alarmFlag           = true;     // RTC alarm true when interrupt (initialized as true for first loop)
volatile bool initSetup           = true;     // False once GNSS messages configured-will not configure again
unsigned long prevMillis          = 0;        // Global time keeper, not affected by Millis rollover
uint32_t      intendedWakeEpoch   = 0;        // For Log Mode 6 to deal with drift
unsigned long syncDuration        = 0;        // How long it took to sync (used for LM 6
unsigned long dates[21]           = {};       // Array with Unix Epochs of log dates !!! MAX 20 !!!
// int           settings[23]        = {};       // Array that holds user settings on SD
char          line[100];                      // Temporary array for parsing user settings
char          logFileNameDate[30] = "";       // Log file name
char          debugFileName[15] = "";         // Debug file name

// DEBUGGING
unsigned long maxBufferBytes      = 0;        // How full the file buffer has been
unsigned long bytesWritten        = 0;        // used for printing to Serial Monitor bytes written to SD
unsigned int  syncFailCounter     = 0;        // Counts RTC sync failures
unsigned int  writeFailCounter    = 0;        // Counts uSD write failures
unsigned int  closeFailCounter    = 0;        // Counts uSD close failures
unsigned int  lowBatteryCounter   = 0;        // Counts # times system sleeps due to low battery
unsigned int  debugCounter        = 0;        // Counts Debug messages
volatile int  wdtCounter          = 0;        // Counts WDT triggers
volatile int  wdtCounterMax       = 0;        // Tracks Max times WDT interrupts
long          rtcDrift            = 0;        // Tracks drift of RTC
enum LedColor { GREEN, RED };
void blinkLed(byte ledFlashes, unsigned int ledDelay, LedColor color = GREEN);
uint32_t cached_chip_id = 0;

struct struct_online {
  bool uSD      = false;
  bool gnss     = false;
  bool rtcSync  = false;
  bool chargedBat = true;
} online;
//////////////////////////////////////////////////////

///////// DEBUGGING MACROS ///////////////////////////
#define DEBUG                     true        // Output messages to Serial monitor
#define DEBUG_GNSS                false       // Output GNSS debug messages to Serial monitor

#if DEBUG
#define DEBUG_PRINTLN(x)          Serial.println(x)
#define DEBUG_PRINT(x)            Serial.print(x)

#else
#define DEBUG_PRINTLN(x)
#define DEBUG_PRINT(x)
#endif

//////////////////////////////////////////////////////
//////////////////////////////////////////////////////

void setup() {

  Serial.begin(115200);
  delay(1000);  // Give time for Serial to start

#if DEBUG
  Serial.println("***WELCOME TO GNSS LOGGER " SOFTWARE_VERSION "***");
  cached_chip_id = *unique_chip_id;
  Serial.print("Unique Chip ID: ");
  Serial.println(cached_chip_id, HEX);
#endif

  //// CONFIGURE INITIAL SETTINGS  ////
  pinMode(LED, OUTPUT);              //
  configureWdt();                    // 12s interrupt, 24s reset period
  checkBattery();                    // IF battery LOW, send back to sleep until recharged
  initializeBuses();                 // Initializes I2C & SPI and turns on ZED (I2C), uSD (SPI)
  configureSD();                     // BLINK 2x pattern - FAILED SETUP
  createDebugFile();                 // Creates debug file headers
  getConfig();                       // Read LOG settings from Config.txt on uSD; 5x - FAILED
  getDates();                        // Read Dates (in unix epoch format) for log mode 5
  configureGNSS();                   // BLINK 3x pattern - FAILED SETUP
  syncRtc();                         // 1Hz BLINK-AQUIRING; 5x - FAIL (3 min MAX)

  // //------------LOG MODE-SPECIFC SETTINGS----------------
  // if (logMode == 1 || logMode == 3) {
  //   configureSleepAlarm();        // Get ready to sleep for these modes
  //   deinitializeBuses();
  // }
  //----------------------------------------------------

  blinkLed(10, 100, GREEN);                 // BLINK 10x - SETUP COMPLETE
  DEBUG_PRINTLN("Info: SETUP COMPLETE");
}
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

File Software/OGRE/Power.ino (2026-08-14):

/* the Low Power functions are adapted from Sparkfun examples LowPower and OpenLog platform. 
 *  and Example6_LowPower_Alarm. 
 *  Sync RTC functionality (sync, getDateTime, printAlarm) modified from A. Garbo GVT.
 *  See license for more details. 
 */

void initializeBuses() {
  pinMode(ZED_POWER, OUTPUT);
  zedPowerOn();
  myWire.begin();
  disableI2CPullups();
  pinMode(PER_POWER, OUTPUT);
  peripheralPowerOn();
  mySpi.begin();
  delay(1);
  #if HARDWARE_VERSION == 2
    pinMode(LED2, OUTPUT);
  #endif
}


void deinitializeBuses() {
  online.rtcSync = false; // This line must be at top! 
  
  if ((logMode == 2 || summerInterval == true) && online.chargedBat == true) { 
    DEBUG_PRINTLN("Info: LOG MODE 2 or SUMMER... No Deinitialize."); 
    return;
  }
  
  myWire.end();           // Power down I2C
  mySpi.end();            // Power down SPI
  zedPowerOff();
  peripheralPowerOff();

  online.gnss = false;   // Clear online/offline flags
  online.uSD = false;
  closeFailCounter = 0;
  lowBatteryCounter = 0;
  
}

// POWER DOWN AND WAIT FOR INTERRUPT
void goToSleep() { // Function from Sparkfun Example6_LowPower_Alarm.ino, see License/Readme.
  if ((logMode == 2 || summerInterval == true) && online.chargedBat == true) { // continuous mode or during summer in mode 6: no sleep
    DEBUG_PRINTLN("Info: LOG MODE 2 or SUMMER... No Sleep."); 
    return;
  }
  
# if DEBUG
  Serial.end();
#endif

  power_adc_disable();    // Disable ADC
  digitalWrite(LED, LOW); // Turn off LED
  #if HARDWARE_VERSION == 2
    digitalWrite(LED2, LOW); // Turn off LED
  #endif

  // Turn peripherals off
  am_hal_pwrctrl_periph_disable(AM_HAL_PWRCTRL_PERIPH_IOM0);
  am_hal_pwrctrl_periph_disable(AM_HAL_PWRCTRL_PERIPH_IOM1);
  am_hal_pwrctrl_periph_disable(AM_HAL_PWRCTRL_PERIPH_IOM2);
  am_hal_pwrctrl_periph_disable(AM_HAL_PWRCTRL_PERIPH_IOM3);
  am_hal_pwrctrl_periph_disable(AM_HAL_PWRCTRL_PERIPH_IOM4);
  am_hal_pwrctrl_periph_disable(AM_HAL_PWRCTRL_PERIPH_IOM5);
  am_hal_pwrctrl_periph_disable(AM_HAL_PWRCTRL_PERIPH_ADC);
  am_hal_pwrctrl_periph_disable(AM_HAL_PWRCTRL_PERIPH_UART0);
  am_hal_pwrctrl_periph_disable(AM_HAL_PWRCTRL_PERIPH_UART1);

  // Disable all pads except LED and PWR CONTROL PINS
  for (int x = 0; x < 50; x++)
  {
    if ((x != LED) && (x != ZED_POWER) && (x != PER_POWER) )
    {
      am_hal_gpio_pinconfig(x, g_AM_HAL_GPIO_DISABLE);
    }
  }

  // Use the lower power 32kHz clock.
  am_hal_stimer_config(AM_HAL_STIMER_CFG_CLEAR | AM_HAL_STIMER_CFG_FREEZE);
  am_hal_stimer_config(AM_HAL_STIMER_XTAL_32KHZ);

  //Power down cache, flash, SRAM
  am_hal_pwrctrl_memory_deepsleep_powerdown(AM_HAL_PWRCTRL_MEM_ALL); // Power down all flash and cache
  am_hal_pwrctrl_memory_deepsleep_retain(AM_HAL_PWRCTRL_MEM_SRAM_384K); // Retain all SRAM

  //Deep Sleep
  am_hal_sysctrl_sleep(AM_HAL_SYSCTRL_SLEEP_DEEP);

  ///////// Waiting for RTC or WDT Interrupt
  ///////// Sleeping...
  ///////// Sleeping...

  // WAKE
  wakeFromSleep();
}
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

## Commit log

2022-02-11 Add LED/Battery Options
2022-02-15 Hardware Documents
    [OGRENET_CAD.f3z]
2022-02-24 Power adjustments
    Power spikes caused by mosfet switching
2022-02-24 More fixes
    Can shorten Delay times since Resistor removed
2022-03-01 fixed battery measurement issues
2022-03-03 Lower Power Consumption
    Reduced load on wakeup for WDT. No longer initializes i2c/spi each wakeup to save power.
2022-03-03 Rearrange power up/down sequence
2022-03-17 updated docs
    [OGRENET_CAD.f3z]
2022-03-20 WDT, LED, DEBUG fixes
    Improvement to WDT (shortened reset period), added additional debug File field, improved LED indicators for failure to sync RTC and failure to read uSD card.
2022-04-25 Update Battery Shutdown Procedure
2022-05-12 Low Power Mode
2022-05-17 Prototype mode improvements
2022-06-23 V1.0.3
    Low battery handling improved
2022-06-23 low battery debug message
2022-06-30 Battery updates
2022-11-18 Update Manufacturing Documentation
    [Enclosure.stl, OGRENET_CAD.f3z]
2022-12-16 now testing file compression /HeatShrink
2023-06-20 telemetry prototype software update
2024-01-04 Minor updates
    New features: (1) Continuous mode generates new files (2) new settings including winter mode and battery threshold
2024-01-11 Big Changes: Log Mode 2 and 6
    Log Mode 2 does not power cycle ZED anymore (RTC sync still happens and is faster due to this); Log Mode 6 uses Log Mode 2 during summer months, and summer months are now user-definable.
2024-06-21 Added debug functionality
    Prints most recent reset code to debug file.
2025-03-17 Battery bug - fixed
    If OGRE monitors battery voltage, it wouldn't have shut down if low voltage if configured in LM 6 or LM 2. This is now corected.
2026-02-06 led upgrades for v2
